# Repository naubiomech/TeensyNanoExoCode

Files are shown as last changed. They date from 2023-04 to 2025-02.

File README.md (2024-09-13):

# Teensy Nano Board

Diagram

This code uses two micronctrollers to control wearable robots. In order to
build the and flash the codebase check [here](Documentation/BUILD_AND_FLASH.md) and [here](https://github.com/naubiomech/TeensyNanoExoCode/blob/main/Documentation/README.md#how-to-deploy). If you would like to
contribute check [here](CONTRIBUTING.md) for more details. 
 
Check out the [Documentation Folder](/Documentation) for more details and C++ info.

Introductory videos on the system, its operation, and getting started can be found [here](https://drive.google.com/drive/folders/1eBydW7si7EmyGxdDkagQktmnZ7M4nHI4?usp=drive_link)

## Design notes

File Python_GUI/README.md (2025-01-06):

# OpenPythonAPI
## Overview

This program can run on any computer/terminal with python 3.12 installed. Libraries needed can be installed via pip (python's module manager)

Open source Application utilizing the OpenExo API to search, connect to, and controll NAU Biomecatronics Lab's OpenExo systems.

This project uses the MIT License.

The purpose of this project is to provide an open source solution for controlling the OpenExo system that is accessible to anyone and free to modify for their needs.

## Minimum System Requirements
**Operating System:**
* Windows 7 or newer
* macOS 10.9 or newer

**Python Version:**
* Python 3.2 or newer

**Hardware:**
* Processor: Dual-core (e.g., Intel Core i3 or AMD equivalent)
* Memory (RAM): 2 GB minimum (4 GB recommended)
* Storage: 100 MB free space (1 GB recommended for large datasets)
* Display: 768x1024 resolution minimum

## Intallation Guide
Video Guide: https://youtu.be/VnQeUM2K6Vg

BLE (Bluetooth Low Energy) is the heart of this project which provides a connection from this API to the exoskeletons. Bleak, a python library is used to handle all BLE operations. To find out more about Bleak click [here](https://bleak.readthedocs.io/en/latest/).

Other libraries that are required include:
 - `matplotlib`
 - `async_tkinter_loop`
 - `pygame`
 - `async_tkinter_loop`
 - `numpy`
 - `bleak`
 - `pandas`
 - `scikit-learn`
 - `micromlgen`
 - `matplotlib`
 - `pygame`
 - `pillow`

To install all of the libraries run the following command in your terminal from the project directory `python .\install_dependencies.py`

## Greneral WorkFlow
### Program control flow

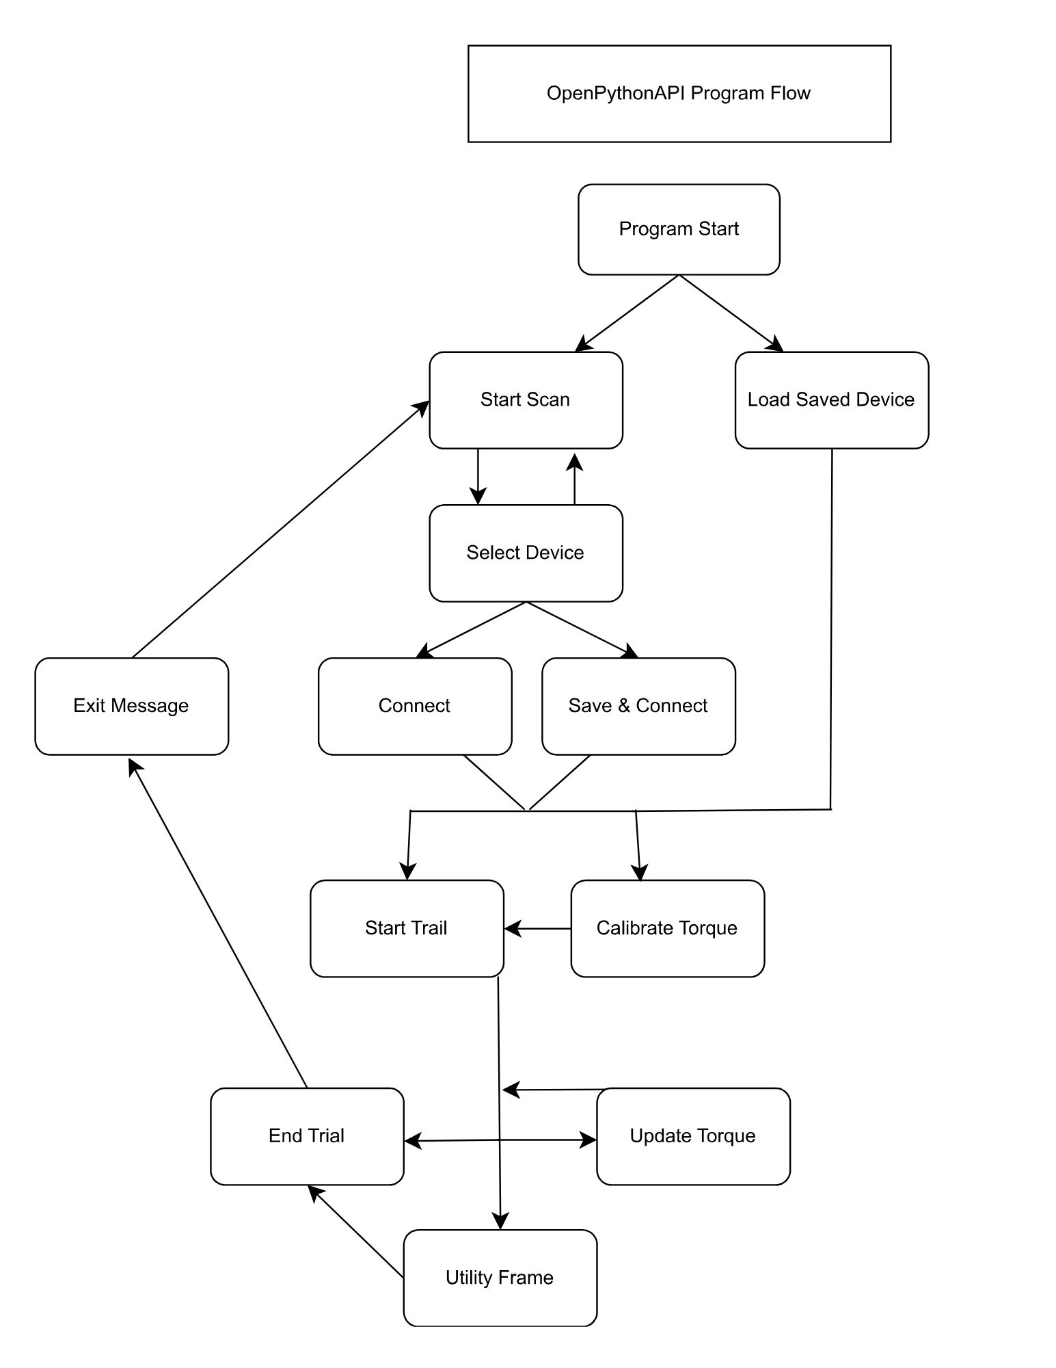
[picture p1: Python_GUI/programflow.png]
Program Control Flow


### Starting the Application
1. Ensure Bluetooth is enabled on your device.

2. Navigate to the project directory in your terminal.

3. Run the command:

`python3 GUI.py`

4. The GUI will launch, presenting various frames for interacting with the system

### Scanning for Devices

1. The application automatically scans for exoskeletons when the scan button is pressed.

2. If Bluetooth is disabled, an OS error will be displayed.

### Navigating the Interface

The GUI consists of several frames, each corresponding to specific functionalities:

* Scan Window: Initiate scanning and connect to devices.

* Active Trial: Monitor active trials and sessions.

* Biofeedback: Access real-time feedback tools.

* Machine Learning: Train and test models for personalized control.

* Update Torque: Change specific attributes of the exoskeleton

### Video Example

https://github.com/user-attachments/assets/6269629e-252b-4e77-b327-0914770ae9e3

## Adding a button

To add a button to the application, follow these steps:

1. Select a Frame: Choose a frame in the PythonApplication\views\ folder where you would like to add the button.

2. Integrate the Button: Here’s an example of how to add a button in a specific frame:

```python
class YourFrame(tk.Frame):
    def __init__(self, parent):
        super().__init__(parent)
        self.create_widgets()

    def create_widgets(self):
        my_button = tk.Button(
            self,
            text="My New Button",
            command=self.my_button_action
        )
        my_button.pack(pady=10)

    def my_button_action(self):
        print("My New Button was clicked!")
```
3. Functionality: Define what the button will do in the my_button_action method.

## Modifying the Graphing

To modify the graphing functionality, you can adjust the BasePlot class and its subclasses. Here's how to do it:

* Limit Points Displayed: In the `update_plot` method, modify the `max_points` variable to control how many points are displayed in the graph:

    ```python
    def update_plot(self, xValues, yValues, secondY, title):
        max_points = -20  # Change this value to display more or fewer points
        xValues = xValues[max_points:]
        yValues = yValues[max_points:]
        secondY = secondY[max_points:]
    ```
* Customize Axes and Titles: In the `update_plot` method, you can also adjust axis labels and titles:

    ```python
    self.ax.set_title(title)
    self.ax.set_xlabel("Time")
    self.ax.set_ylabel("Value")
    ```
* Implement Animation: Each plot subclass (e.g., `TopPlot`, `BottomPlot`) has an animate method that gathers data and updates the plot. Modify this method to change how data is sourced and displayed.

* For graph variable modification, refer to the Biofeedback graph description bellow.

## Adding a New Frame

To add a new frame to the application, follow these steps:

### Step 1: Create the New Frame Class

Create a new Python file in the views folder (e.g., newFeature.py).

Use the following template to define your new frame:

```python
    import tkinter as tk

        class NewFeature(tk.Frame):
        def __init__(self, parent, controller):
            super().__init__(parent)
            self.controller = controller

            label = tk.Label(self, text="New Feature Frame", font=("Arial", 24))
            label.pack(pady=20)

            button = tk.Button(self, text="Go to Scan Window",
                                command=lambda: controller.show_frame("ScanWindow"))
            button.pack(pady=10)
```
### Step 2: Update the ControllerApp Class

Open your main application file.

Import the new frame at the top:

`    from views.newFeature import NewFeature`

Add the new frame to the frames dictionary in the ControllerApp class:
```python
    for F in (ScanWindow, ActiveTrial, UpdateTorque, BioFeedback, MachineLearning, NewFeature):
```
### Step 3: Navigate to the New Frame

You can add a button in any existing frame to navigate to the new feature:
```python
    button = tk.Button(self, text="Go to New Feature",
                    command=lambda: controller.show_frame("NewFeature"))
    button.pack(pady=10)
```
## Biofeedback Frame
### Purpose

The Biofeedback frame provides visual and auditory feedback to users during training or analysis sessions. It aids participants in achieving specific performance goals by leveraging real-time sensor data.

### Signal Used in Biofeedback

1. Biofeedback currently utilizes force-sensitive resistors (FSRs) to monitor plantar pressure or estimated ankle power from exoskeleton sensors, but any sensor can be used.

2. The FSR data signal is accessed via the variable:

    `self.master.controller.deviceManager._realTimeProcessor._chart_data`

3. To switch between left and right leg signals, the variable updates dynamically based on the user’s selection 
    `._chart_data.leftFsr` or `._chart_data.rightFsr`

### Modifying the Signal

To modify the signal used in the biofeedback game:

1. Locate the FSRPlot class in the `chart.py` file.

2. Update the data source to the desired signal by modifying the variable:
    
    `self.master.controller.deviceManager._realTimeProcessor._chart_data` 

### Features and Buttons

#### Graphing

1. Graph Display: Visualizes pressure sensor data for real-time monitoring.

2. Target Lines: Displays a goal threshold on the graph when a target value is set.

#### Buttons

1. Back: Returns to the Active Trial frame.

2. Left/Right Leg Toggle: Switches the graph display between left and right leg FSR data.

3. Set Target Value: Opens a dialog box to input a target value for training.

    * Enables tracking progress toward specific performance goals.

4. Reset Target Value: Clears the target value and removes the goal line from the graph.

5. Mark Trial: Marks a specific event during data collection for later analysis.

6. Recalibrate FSRs: Initiates recalibration of the force-sensitive resistors to improve accuracy.

#### Notifications

1. Auditory Feedback: Plays a notification sound (e.g., `notification.wav`) when the user achieves a target.

2. Visual Feedback: The background temporarily changes color to indicate a successful target hit.

### Customization

To add or modify features in the Biofeedback frame, refer to the BioFeedback class in `biofeedback.py`.

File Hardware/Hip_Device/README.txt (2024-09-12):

Guiding Documentation to Assembling the device can be found at: https://drive.google.com/drive/folders/1gUSrXI882WxxylISEO5OPi-XwMUpgyXN?usp=drive_link

The Download for the CubeMars Motor Setup tool can be found in the same location.

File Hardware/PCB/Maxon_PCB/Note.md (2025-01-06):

More information on Maxon Motor Compatability (updated software, PCB, and hardware) coming soon!

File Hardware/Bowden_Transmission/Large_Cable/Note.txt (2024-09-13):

For the AK80 and Ak70 motors, if you are pursuing applications that require 
torque mangiutdes over 30 Nm, we recommend using a larger steel cable than the ones provided.

This necessitates a few modifications to the bill of materials and parts for the system, namely different:

Cable-Chain Interfaces
Bowden Tubes
Steel Cable
Crimps

We have included an updated BOM with this information to help you orient to that, the assembly process reamins the same

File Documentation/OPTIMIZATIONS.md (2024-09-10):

## Optimizations
- SPI direct memory access. Should change SPI time from 20 &mu;s per byte to the time to write the memory.
    - Teensy Datasheet 48.2.1 
        - Configure SPI
        - Teensy as controller and Nano as peripherial.
    - At top of loop teensy
        - Teensy flushes TX buffer and places fresh data data on TX Buffer.
        - Read if there are new messages from Nano and que completed messages.  Nano will read fresh data when this happens.
        - Teensy processes the que of new complete messages.  This should be a couple of messages and should be fine as the data sent will likely be smaller than data received.
        - Teensy runs the rest of the control loop.
    - Nano would place messages on tx buffer as bluetooth messages come in.
        - If the Nano is placing data when the Teensy reads the message will be sent over incomplete and will need to place the rest of the message afterwards which the Teensy will append when the next read happens.
        - Will need a message complete indicator at end of message.
        - Teensy que will also need a message complete flag to know if it needs to precess the message or if the message is incomplete start the next read by appending the rest of the message here. 

- BLEparser change from char representation to num bytes, expect 3 to 6x speed up.
    - This should be pretty straight forward as it can pretty much follow how messages are packed for the SPI.
    - I am not sure what issues will arise on the app side.
        - On the app you could just add a converter from num to char if you want to be lazy, but presumably you already have a char to num converter so I would recommend just cutting that out and fixing the stuff that breaks.
    
- CAN direct memory access, should cut about 250 &mu;s per motor.  Will still need a loop period of at least 250 &mu;s for the motors to return data.
    - https://www.pjrc.com/teensy/IMXRT1060RM_rev3.pdf 
        - CH 44
    - 6 mailboxes between TX and RX may have issues for a 4 motor setup without using a CAN bus per leg.  
        - All the complication with the limited mailboxes can be simplified by just using separate CAN buses for each leg, see other optimization below.  I have included how you could do it by switching mailboxes below, but don't do that if you don't have to.
            - Setup and Debug this with a bilateral uni-joint or unilateral multi-joint system so you can keep the motor count below 3 so you don't have to fiddle with all the mailbox shifting.  Then just setup the CAN2 below.
        - Can potentially use an ISR to mitigate this with a bit of loss in performance but will still be a big jump from where we are.
        - Can potentially switch mailbox type after emptied. Pair first TX (44.7.2) with first RX(44.7.4). When first TX is cleared becomes RX for next TX, or similar.  **DON'T WRITE A TX WITHOUT A CORESPONDING RX**.  You can write based on priority to help, highest priority first so you know it will return first.
            - This doesn't have to be first TX becomes second RX but you can play around to see what works.  Could have two TX RX pairs and two unpaired TX then the first two TX are emptied, change them to the RX for the unpaired TX and fill the second set of TX for writing.
        - 44.7.6 will also be useful.  In addition to the registers/memory map at the end.
    
- CAN bus per leg after DMA, roughly cut CAN time in half. Main control may be limiting time at this point at about 600&mu;s. Write at top, do controls, read at bottom.
    - Basically just follow above but with CAN2.  
    - Will need to update CAN code to make the CAN selectable 
    - Will need to attach a CAN object to the Leg instance rather than the Exo instance.

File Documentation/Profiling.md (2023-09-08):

Profiling is used to determine how long it takes for the computer to run your code. 
Typically more advanced software is used to automatically determine how long
each section of code takes to run, but Arduino does not provide any profiler software. 

To profile a section of code call micros() above the section of code and micros() below 
the section of code. Then Serial.print() the difference. ie:
        float start_time = micros();
        // The section of code
        float end_time = micros();
        Serial.print("Elapsed time in microseconds: ");
        Serail.println(end_time - start_time);

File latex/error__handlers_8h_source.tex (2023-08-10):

\doxysection{error\+\_\+handlers.\+h}
\hypertarget{error__handlers_8h_source}{}\label{error__handlers_8h_source}\index{ExoCode/src/error\_handlers.h@{ExoCode/src/error\_handlers.h}}
\mbox{\hyperlink{error__handlers_8h}{Go to the documentation of this file.}}
\begin{DoxyCode}{0}
\DoxyCodeLine{00001\ \textcolor{preprocessor}{\#ifndef\ ERROR\_HANDLERS\_H}}
\DoxyCodeLine{00002\ \textcolor{preprocessor}{\#define\ ERROR\_HANDLERS\_H}}
\DoxyCodeLine{00003\ }
\DoxyCodeLine{00004\ \textcolor{preprocessor}{\#if\ defined(ARDUINO\_TEENSY36)\ \ ||\ defined(ARDUINO\_TEENSY41)}}
\DoxyCodeLine{00005\ }
\DoxyCodeLine{00006\ \textcolor{preprocessor}{\#include\ "{}\mbox{\hyperlink{_exo_data_8h}{ExoData.h}}"{}}}
\DoxyCodeLine{00007\ \textcolor{preprocessor}{\#include\ "{}\mbox{\hyperlink{_exo_8h}{Exo.h}}"{}}}
\DoxyCodeLine{00008\ \textcolor{preprocessor}{\#include\ "{}\mbox{\hyperlink{error__types_8h}{error\_types.h}}"{}}}
\DoxyCodeLine{00009\ \textcolor{preprocessor}{\#include\ "{}\mbox{\hyperlink{uart__commands_8h}{uart\_commands.h}}"{}}}
\DoxyCodeLine{00010\ }
\DoxyCodeLine{00011\ \textcolor{comment}{//\ Handles\ errors}}
\DoxyCodeLine{00012\ \textcolor{keyword}{namespace\ }error\_handlers}
\DoxyCodeLine{00013\ \{}
\DoxyCodeLine{00014\ }
\DoxyCodeLine{00015\ \ \ \ \ \textcolor{keywordtype}{void}\ soft(Exo*\ exo,\ \mbox{\hyperlink{class_exo_data}{ExoData}}*\ exo\_data,\ \textcolor{keywordtype}{int}\ error\_code)}
\DoxyCodeLine{00016\ \ \ \ \ \{}
\DoxyCodeLine{00017\ \ \ \ \ \ \ \ \ \textcolor{comment}{//\ TODO:\ Recalibrate/Warn\ user}}
\DoxyCodeLine{00018\ }
\DoxyCodeLine{00019\ \ \ \ \ \ \ \ \ \textcolor{keywordflow}{return};}
\DoxyCodeLine{00020\ \ \ \ \ \}}
\DoxyCodeLine{00021\ \ \ \ \ \textcolor{keywordtype}{void}\ hard(Exo*\ exo,\ \mbox{\hyperlink{class_exo_data}{ExoData}}*\ exo\_data,\ \textcolor{keywordtype}{int}\ error\_code)}
\DoxyCodeLine{00022\ \ \ \ \ \{}
\DoxyCodeLine{00023\ \ \ \ \ \ \ \ \ exo\_data-\/>\mbox{\hyperlink{class_exo_data_a2aa97c53cd67d549d14b349cf1b46f0e}{for\_each\_joint}}([](\mbox{\hyperlink{class_joint_data}{JointData}}*\ joint\_data,\ \textcolor{keywordtype}{float}*\ args)\ \{\textcolor{keywordflow}{if}\ (joint\_data-\/>\mbox{\hyperlink{class_joint_data_ac92eaeab50564303d8c8ca0febd44c12}{is\_used}})\ joint\_data-\/>\mbox{\hyperlink{class_joint_data_afaead532774a6d60394f3667838d61d1}{motor}}.\mbox{\hyperlink{class_motor_data_a4b909a13e4ac0eb7c3f05a1de2b0dc60}{enabled}}\ =\ 0;\});}
\DoxyCodeLine{00024\ \ \ \ \ \ \ \ \ \textcolor{keywordflow}{return};}
\DoxyCodeLine{00025\ \ \ \ \ \}}
\DoxyCodeLine{00026\ \ \ \ \ \textcolor{keywordtype}{void}\ fatal(Exo*\ exo,\ \mbox{\hyperlink{class_exo_data}{ExoData}}*\ exo\_data,\ \textcolor{keywordtype}{int}\ error\_code)}
\DoxyCodeLine{00027\ \ \ \ \ \{}
\DoxyCodeLine{00028\ \ \ \ \ \ \ \ \ exo\_data-\/>\mbox{\hyperlink{class_exo_data_a2aa97c53cd67d549d14b349cf1b46f0e}{for\_each\_joint}}([](\mbox{\hyperlink{class_joint_data}{JointData}}*\ joint\_data,\ \textcolor{keywordtype}{float}*\ args)\ \{\textcolor{keywordflow}{if}\ (joint\_data-\/>\mbox{\hyperlink{class_joint_data_ac92eaeab50564303d8c8ca0febd44c12}{is\_used}})\ joint\_data-\/>\mbox{\hyperlink{class_joint_data_afaead532774a6d60394f3667838d61d1}{motor}}.\mbox{\hyperlink{class_motor_data_a4b909a13e4ac0eb7c3f05a1de2b0dc60}{enabled}}\ =\ 0;\});}
\DoxyCodeLine{00029\ \ \ \ \ \ \ \ \ \textcolor{keywordflow}{return};}
\DoxyCodeLine{00030\ \ \ \ \ \}}
\DoxyCodeLine{00031\ \}}
\DoxyCodeLine{00032\ }
\DoxyCodeLine{00033\ \textcolor{preprocessor}{\#endif}}
\DoxyCodeLine{00034\ }
\DoxyCodeLine{00035\ \textcolor{preprocessor}{\#endif\ }\textcolor{comment}{//\ defined(ARDUINO\_TEENSY36)\ \ ||\ defined(ARDUINO\_TEENSY41)}}

\end{DoxyCode}

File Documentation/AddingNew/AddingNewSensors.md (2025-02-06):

# Adding New Sensors

## Overview
In our codebase, sensor integration varies depending on the sensor. Below, we list some of the sensors we've tested or integrated that are compatible with our codebase:
- **Analog input**
    - Force sensitive resistor
    - Torque sensor (strain gauge)
    - Angle sensor (AS5600; hall effect)
- **Bus protocol**
    - I2C (Teensy-Nano communication)
    - UART (Teensy-Nano communication)
    - CAN (Teensy-Motor communication)
    - SPI (Teensy-SD Card interface)

Here, we'll demonstrate how the Teensy communicates with sensors using an example of an analog input sensor and another example with the I2C protocol.

---

## Analog input
For an analog sensor, such as the torque sensor we used for exoskeleton torque feedback control, the fundamental operation involves using `analogRead()` on the signal pin to get the sensor reading (or its amplified value):

```
float current_reading =  analogRead(_pin)*torque_calibration::AI_CNT_TO_V;
```

### Notes from PJRC:
- None of the pins on the Teensy are 5-volt tolerate, and the input voltage range is fixed at 0 to 3.3 volts.
- `analogReference()` has no effect on Teensy 4.1

*Sidenote*: If you need to use `digitalRead()`, make sure to set the appropriate pin mode using `pinMode()` with values such as `INPUT` or `INPUT_PULLUP`. Refer to the user manual of the sensor or peripheral in use.

### More examples on `analogRead()`
The following `.cpp` files utilize `analogRead()`:
- `AnkleAngles.cpp`
- `FSR.cpp`
- `TorqueSensor.cpp`

### Available analog pins
If you're using our reference printed circuit boards (PCB), check the PCB design documentation for the list of available analog pins. You can always use stacking headers for Teensy 4.1 to make certain pins easier to access.

---

## Bus protocols
Unlike data links that use analog signals, a bus acts as a highway for digital signals carrying encoded messages, enabling much faster data transmissions at higher frequencies. You can find a comparison of some of the bus protocols used in our codebase [here](https://www.totalphase.com/blog/2021/12/i2c-vs-spi-vs-uart-introduction-and-comparison-similarities-differences/ "I2C vs SPI vs UART").

### I2C in our codebase—A detailed example
Noah Enlow put together some great documentation detailing how I2C works in our codebase, and we're excited to share it here.

<details open>

  <summary><strong>Click to fold</strong></summary>

- I2C works by sending a series of bytes that represent the information you're wanting to send. The Wire library in arduino does not automatically interpret the bytes being sent/recieved into the intended data type (e.g. float or int). Therefore, in order to send data over I2C with the wire library, the data must be converted into its respective representation in bytes. The simplest and most efficient way to do this is to use a union. 

- Unions in arduino (and C++) function similar to structs. However, with unions, the data stored within is stored in a single location in memory and can be accessed as any data type desired (such as float or int). Thus, a union allows you to access the same raw data in multiple ways. 

- This is useful for sending data over I2C because now we can collect our data from a sensor (say float data from an accelerometer), store it in a union, and then access that same data as bytes when we're ready to send it via I2C. On the receiving device, we essentially do the opposite. We receive the incoming bytes into a union, and then access the data as floats again.
The scheme is:
```
    float -> convert to bytes -> send over I2C -> receive as bytes -> convert back to float
```
- Below is a demonstration of how to send float data over I2C using a union (the process is identical for other data types such as ints or doubles):

    1. First define the union: 
    ```
        union Data                      # Data is the name of the union
        {
            float data_as_float;        # Representation of the data as a float
            byte data_as_bytes[4];      # Represntation of the data as a vector of bytes (must specify the size, floats are 4 bytes)
        };
    ```

    2. Now store the data you'll be sending:
    ```
        Data.data_as_float = data_to_be_sent;	# data_to_be_sent is a dummy variable representing the data you want to send
    ```

    3. Send via I2C using the Arduino Wire library:
    ```
        void sendEvent()                         # sendEvent() is called in your main loop whenever you are ready to send the data
        {													
            Wire.write(Data.data_as_bytes, sizeof(Data.data_as_bytes));
        }
    ```

- Now to recieve the data that has been sent. We'll create an identical union on the device requesting the data (primary) to make it more intelligible, however the union need not be identical.
    1. Define a union on the device receiving the data:
    ```
        union Data                      # Data is the name of the union
        {                	
            float data_as_float;        # Representation of the data as a float
            byte data_as_bytes[4];      # Representation of the data as a vector of bytes (must specify the size, floats are 4 bytes)
        };
    ```

    2. Now request the data from the peripheral (secondary) device, which in this case is the one doing the sending. Because the data is coming in as individual bytes, we'll need a for loop to iterate through those bytes and append them to the vector of bytes contained in the union we just defined.
    ```
        Wire.requestFrom(PERIPHERAL_ADDRESS, 4);
        for(int i=0; i<4; i++)
        {
            Data.data_as_bytes[i] = Wire.read();
        }
    ```
    3. Now to access that data as a float again:
    ```
        float data_recieved = Data.data_as_float;
    ```

- In summary, a union was created on our peripheral device (the device sending) to store the float data and send it as bytes over I2C. Another identical union was created on our primary device, which in this case is the one we want to recieve the data. A for loop is used on the primary to iteratively append the bytes being recieved to the byte-type variable in the union. Once this is done, the data recieved can then be accesed as a float again through the union.

</details>

---

### More examples on bus protocols
The following `.cpp` or `.h` files utilize I2C:
- `Battery.cpp`
- `I2CHandler.h`
- `RealTimeI2C.cpp`
- `ThIMU.h`

The following `.cpp` file utilize SPI:
- `ParamsFromSD.cpp`

The following `.cpp` or `.h` files utilize UART:
- `ble_commands.h`
- `ComsMCU.cpp` and `ComsMCU.h`
- `ErrorReporter.h`
- `Exo.cpp`
- `uart_commands.h`
- `UARTHandler.cpp`

The following `.cpp` or `.h` files utilize CAN:
- `CAN.h`
- `Motor.cpp`

### Available pins for bus protocols
If you're using our reference printed circuit boards (PCB), check the PCB design documentation for the list of available pins for bus protocols. You can always use stacking headers with Teensy 4.1 to make certain pins easier to access.

---
To ensure a sensor readings are accessible from various locations, we've created the following procedures to help you embed your new sensor into the codebase.
## Location—Where should I write the sensor code?
Because the sensors don't have a common interface it is a bit more straight forward to add new ones.
The main things you will need to decide is what part of the system makes the most sense for the part to live, e.g. exo, side, joint.

## Create the Sensor
The sensor should be its own class.
You will need to create a .h and .cpp file in the src folder.
The sensor class will have all the functions that you need to use the class, below you can find an example to build from.
This example is an outline of what would be in the header(.h) file.

```
class CLASS_NAME
{
    /*
     * public functions are ones that can be called from outside the class.
     */
    public: 
        /*
         * Constuctor for the class
         */
        CLASS_NAME(int pin);// you may not need the pin if it doesn't use an analog input.
        
        /*
         * Checks if the sensor needs to be calibrated and returns if the calibration is done.
         * This should be called every time the containing system is run.
         * Depending on your system you may not need to calibrate.
         */
        bool calibrate(bool do_calibrate);
        
        /*
         * Used to read the sensor and returns the value.
         * If you need multiple returns you will need to pass the place the date will go by pointer: 
         * void read(float* val0, float* val1);
         * Where it will be called using:
         * read(&place_to_store_val0, &place_to_store_val1);
         */
         float read();
    /*
     * Private functions and variables can only be called from within the class.
     */
    private:
        
        /* 
         * Sample private function this will be very dependent on what the system needs.
         */
        void _sample_function();
        
        // The pin the sensor is connected to.
        int _pin;
        
        // sample private variable for the sensor.
        float _sample_var;
};
```

## Migrating to the Main Code.

### Board.h
For each board that will use the sensor add the pin that each sensor will use.
If there are four sensors you will need to define 4 pins.
This assumes it is an analog sensor, if you are using a different type of sensor you can define the things that sensor needs here.
Make sure that that pin is free, this should be easier if you design the PCB first.

### System Containing Sensor Data .h
Create a variable to store the the data from the sensor.
If the sensor will be at the side level this will be in the SideData class, if it is the joint the JointData class, etc.
Additionally if the sensor will need to be calibrated make a variable to store that state;
```
float sensor_reading;
bool sensor_calibrate;
```

### System Containing Sensor Data .cpp
In the constructor related the the .h file you just modified, initialize the value to to what you want it to start at, this will often be 0.

```
sensor_reading = 0;
sensor_calibrate = false;
```

### System Containing Sensor.h
This will be Side.h if the sensor is at the side level or Joint.h if it is at the joint level, etc.
Add the include for the sensor, ```#include Sensor.h```, that you created.
Within the class; Side, Joint, etc.; declare an instance of the class ```SensorClass new_instance_of_sensor;```
Create as many instances as you need.

### System Containing Sensor.cpp
1. Within the .cpp file related to the .h file you just changed you need to call the constructor for the instances of the class you just declared.
This will be done in the initializer list.
For example for a joint level sensor:
```
Joint::Joint(config_defs::joint_id id, uint8_t* config_to_send)
: motor(id, config_to_send)
, controller(id, config_to_send)
, new_instance_of_sensor(pin_to_use)
{
```

2. Add a call to the sensor.read() in the containing classes read referencing the sensor data we already made.
For a joint level sensor:
``` 
_joint_data->sensor_reading = new_instance_of_sensor.read();
```

3. Add a call to the sensor.calibrate(do_calibrate) in the containing classes read referencing the sensor data we already made.
For a joint level sensor:
``` 
_joint_data->sensor_calibrate = new_instance_of_sensor.calibrate(_joint_data->sensor_calibrate);
```

This will get called every time the joint is run and if the calibrate variable is set to true will calibrate the sensor.

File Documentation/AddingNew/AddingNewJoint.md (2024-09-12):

# Adding a new joint

## Exocode.ini
1. Line 118: Add joint to the debug statement determining if it is used.
2. Line 148: Add joint to if statements relating to whether or not the joint is used
	- Copy the if statements for the left and right side for one joint (e.g., hip) and paste below last joint
	- Modify the joint to be named after the new joint you are adding. 
3. Line 398: Add in calibrate torque sensor and enable motors for the joint while in headless mode
	- Copy the formatting from another joint, make sure to do both left and right side.
4. Line 540: This section sets the controller for each joint (while in headless mode), copy the formatting for one joint and rename it to your new joint
	- Need to pull in the default controller information from the config
	- Then set the controller based on this configuration information

## ParseIni.h
1. Update exo_name in the config_defs namespace, make sure to encompass any configuration you would want with that joint (e.g., bilateral, unilateral, multi-joint)
2. Update JointType in the config_defs namespace
3. Update joint_id to utilize the proper byte for the new joint (see comment in code)
	- make sure to update the left and right joint information following the format as well. 
4. Add a new enum class for the joint's controllers following the other joints' formatting
	- Add in any controllers associated with the joint if there are any ready, you can always come back to this following "AddNewController"
5. Update the static const int variables at the end of the config_defs namespace to account for the new joint.
6. In config_map namespace, update the IniKeyCode exo_name to account for all the configurations made in the exo_name enum class in config_defs
7. In config_map namespace, add in a new IniKeyCode for the joint's controllers (following the format for the other joints)
	- Make sure to update the terminology of the entire section (i.e., the section after config_defs:: in the main text of it
8. Update the ConfigData struct at the end to match 
 
## ParseIni.cpp
1. Line 174 -> Onward: Copy template in each section to add in new joint so that it is formatted same as other joints.

## ExoData.h
1. In the functions "for_each_joint", add in the new joint following the format of the previous joints
    
## ExoData.cpp
1. In the function "get_used_joints" (36), add in the new joint following the format of the other joints already there, make sure to do both the left and right sides
2. In the function "get_joint_with" (59), add in the new joint following the format of the other joints already there, make sure to do both the left and right sides
3. Similarly, in the function "print" add in the prints of the new joint for each side (left and right) following the establish formatting.

## UART_commands.h
1. Update the function "get_config" (Line 196) with the config_defs you added in ParseIni.h, refer to that file and look at the added "static const int" at the end of the config_defs namespace
2. Similarly, update the function "update_config" (Line 227) with the config_defs you added in ParseIni.h, refer to that file and look at the added "static const int" at the end of the config_defs namespace
3. In "get_real_time_data" (Line 306), add in a new case in the switch statement corresponding to the bilateral configuration of the joint and for any multi-joint instances. You can send up to 10 data points at a time using the established formmating.

## Side.h
1. Create Joint object specific to the joint that you are adding (Line 158, is where the other joint objects are specificed, follow their formmating)

## Side.cpp
1. Add in the new joint object you just created in the .h file into the constructer of the side following the format of the other joints in the constructer 
2. In the "disable_motors" function (Line 58), add in the new joint following the formatting of the other joints.
3. In the "read_data" function (Line 98), add in an if statment at the end (Line 142) that reads the data specific to the joint object (see other joints for formatting)
4. In the "check_calibration" function (Line 161), add in a if statment at the end of the end of the function (Line 189) that checks the calibration specific to the new joint object (see other joints for formatting)
5. In the "update_motor_cmds" function (Line 534), add in a new if statement at the end that runs the new joint functions (see other joints for formatting)

## SideData.h
1. Line 42: Create a new instance of jointdata and create an object for it for your new joint (see other joints for formatting)

## SideData.cpp
1. Add in the new joint object you just created in the .h file into the constructer of the sidedata following the format of the other joints in the constructer 
2. On the last line add in a new statement reconfiguring the joint you just added (see other joints for formatting). 

## Joint.h
1. Create a class specific to the joint, make sure it inherits the public _joint class
	- Make sure to include a joint specific constructor and destructor and the two essential functions "run_joint" and "set_controller" in the public section.
	- In the private section call instances of the controller class for those specific to the joint and create new objects for those classes
	- Aka copy what the other joints did and change the names and controllers

## Joint.cpp
1.	Add the new joint to the Joint Debug statement (Line 40) in the _Joint constructor at the begining
2. 	In the function "get_torque_sensor_pin" add a new case to the switch statment specific to your added joint following the format of the other joints
3.	Similarly, in the function "get_motor_enable_pin", add a new case to the switch statement specific to your added joint.
4. 	Add in the new joint class following the format of the other joints
	- Make sure to include all the controller instances in the initializer list in addition to the _Joint instance 
	- Update the debug statements to refelct the newly added joint
	- Update the Switch Case that creates an object for the specific motor type 
	- Update the call of the "set_controller" function at the end of the constructor
	- Update the "run_joint" function 
		- update the debug statements, the rest is non-joint specific 
	-Update the "set_controller" function 
		- Update debug statement
		- Update switch case for controller ID

## JointData.cpp
1. Update the switch statement in the JointData initializer to include the new joint (Line 31) 
	- Include the portion that sets the value for "is_used" and the if statment to flip the direction 
	- Follow the format of the other joints in this section 
2. Repeat this process for the "reconfigure" function 

## Motor.cpp
1. Update the switch statment in the motor initializer (Line 39) to include the new joint

## MotorData.cpp
1.	Update the switch statement in the initalizer (Line 16) to include the new joint
	- Include both the gearing and the flip direction portions
2. 	Repeat this process for the "reconfigure" function 

## ControllerData.cpp
1.	Update the switch statement in the constructor (Line 16) to include the new joint
2. 	Repeat process for the "reconfigure" function (Line 56)

## Controller.cpp
1.	Update the switch statement in the constructor of _Controller to incorporate the new joint (Line 35)

## ble_commands.h
1. In the function "new_trq" update the joint_id mapping to encompass the new joint (make sure to do both left and right side)
	- Make sure you update the joint id number in these statments to follow a logical order (e.g., left_hip = 1, left knee = 2, left ankle = 3, left elbow = 4, ....)
2. Update the if statement associating controller data with the joint ID

## ParamsfromSD.h
1.	In the controller_parameter_filenames namespace, add in a ParamFilenameKey for the new joint and associate the appropriate controllers

## ParamsfromSD.cpp
1.	In the "print_param_error_message" function, update the switch statment to include the new joint
	- Make sure to update the actual switch statment itself during this process (Line 10) in addition to adding the new case 
2. In the "set_controller_params" function 
	- Copy a case of the switch statement from another joint below the last added joint, update any reference to the specific joint (e.g., elbow, ankle,...) to your new joint
	- There is a lot going on here so make sure you did not miss any reference to the specific joint in this section. 
## RealTimeI2C.h
1.	In the rt_data namespace update the static int RT_LEN to include the configurations you added to "get_real_time_data" in uart_commands.h

## StatusDefs.h
1. In the messages namespace, update the error messages with the joint you are adding
	- Torque Sensor, Motor, Controller portions for both side (left, right)
	- Make sure to go back and update the numbering 
2. Update the nomenclature of the remaining "error_to_be_used" if there are any 

## StatusDefs.cpp
1.	Update the switch statment in "print_status_message" to include the new joint
	- Torque Sensor, Motor, Controller for both sides (left, right)

## StatusLED.h
1.	Update IdxRemap status_led_idx in the status_led_defs namespace with the new joint, follow the other joints for formatting
2. 	Remove the no longer valid "error_to_be_used_#" sections 

## Config.ini
1.	Copy the information for one joint setting (e.g., bilateralHipAnkle) and add paste it later on 
2. 	Rename the newly added formatting for your newly added joint
3. 	Update the contained information appropriatly

## SD Card
1. Make a jointControllers folder with the .csv for the controllers specific to the joint

## Python GUI - ActiveTrialSettings.py
1. Find the section titled "jointMap"
	- Add in the new joint name and incrament the int value in the section following the format of the other joints.
2. In the UpdateTorque Class, update the string list in "values" under the section labeled "Joint Select" with the joint name (e.g., Left elbow, right elbow)

## Python GUI - exoDeviceManager.py
1. Find "jointDictionary" under the ExoDeviceManager Class
	- Update the directory with the joint numbers you added in "ActiveTrialSettings" and associate with the Motor ID number you set the motor to via the RLink and in the software
	- Follow the format of the other joints (e.g., 1: 33. 0 = "Left Hip with an ID of 33")

## Done
It should now be good to go.

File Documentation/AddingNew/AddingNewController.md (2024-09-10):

# Adding a new controller

## parseIni.h
1. Go to the config_defs namespace and the joint(s) you are creating a controller for and add it to the enum class so we can reference it.
2. Go to the config_map namespace and add for the joint(s) you are creating a controller for and add the name that will be used in the config.ini file.

## ControllerData.h
1. Go to the controller_defs namespace and add a namespace for your controller following the template from the other controllers
    - Create idx values that will be used to access the different parameters (remember this is 0 indexed)
    - Add a num_parameter value that stores the number of parameters the controller needs.
    - if this number is larger than the max_parameters in controller_defs, change max_parameters to your value. 

## Controller.h
1. Under Controller.h create a new controller that inherits the _Controller class.
    - this must have:
        - A constructor that takes in the joint id and exo_data pointer.
        - A destructor
        - And a calc_motor_cmd() function that returns the torque command in mNm.
    - Additional private functions or variables can be added as needed but the only calls to a controller will be to the three required functions.

## ControllerData.h
1. This section is optional, at the bottom of ControllerData.h you can add any variables for your controller that you would like to be able to plot, these would be in place of the variables defined in Controller.h. 
	- To assign value to these parameters in Controller.cpp, you need to use the following formatting:
		- controller_data->NAMEOFVARIABLE = VALUE;
		
## Controller.cpp
1. Define all the functions for the controller.  
    - An initializer list for _Controller will be needed when calling the constructor.  
    
## Joint.h
1. Under the joint(s) (hip, knee, ankle) the controller is valid for, add an object to the new controller.

## Joint.cpp
1. For the joint(s) the controller is valid for:
    1. Add the constructor for the object you just added to the initializer list.
    2. In set_controller(), add the controller to the switch case, referencing the joint controller namespace in the config_defs namespace.  
        - Use the existing controllers for the template
        - This changes which controller object the _controller pointer is using.
        - Don't forget to add the 'break;' at the end of the switch case!
	- Note: The switch case references the config_defs name and the value passed to _controller references the object created in Joint.h

## Create parameter file
1. In the SDCard folder go to the joint your controller is for.
2. Create a new parameter csv file, I would recommend just copying one of the existing ones
3. The first cell in the first line is the number of lines in the header.  Parameters will start being read after this number of lines.
4. The first cell in the second line is the number of parameters to read, this should match what you put in ControllerData.h.  This was easier than trying to get the reading a full line of floats to be robust.
5. After the header, put the parameter sets you would like to use, one set per line.  The parameters should be listed in the index order from ControllerData.h.  The first set will be default.
6. If the controller is multi joint copy to the other joint folders.

## ParamsFromSD.h
1. In the controller_parameter_filenames namespace go to the appropriate joint
2. Link the controller id from config_defs and the path on the SD card for the parameter file you just created.

## uart_commands.h
1. This section is optional, if you want to plot or save one on of the variables you created in ControllerData.h:
	- In get_real_time_data()
		- Find the case for the joint you are using the controller for (e.g., bilateral_hip)
		- Assign the variable to one of the data spots in the rx.msg (e.g., rx_msg.data[0])
			- If the variable is specific to the controller, use the following formatting:
				- rx_msg.data[#] = exo_data->NAME_side.JOINT.controller.VARIABLENAME;
					- Here: NAME_side should either be left_side or right_side, JOINT should be the joint you are working with, and VARIABLENAME is the name of the variable you want to plot.
			- You can also plot variables specific to a side (defined in SideData.h) using the following formatting:
				- rx_msg.data[#] = exo_data->NAME_side.VARIABLENAME;

## Done
It should now be good to go.  You will need to change the controller and update the parameters.

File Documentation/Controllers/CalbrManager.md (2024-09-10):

# Calibration Manager Controller

## Description
This controller applies a small, constant torque while printing statements of relevance (command value/sign, torque sensor value/sign, angle sensor value/sign) to the Arduino Serial Monitor. 

## Parameters
There are no user defined parameters associated with this controller. 

## Purposes
After you have built an exo, one of the first things to check is the motor directions and the signs (positive/negative) of any of your external sensors (torque, angle, etc.). 
Having correct motor directions is important as it allows the exo controller designers to focus on the control itself, knowing that, if calibrated properly before use, the exo assistance will always be in the designed directions. 
The same principle applies for the sensors involved with control. Since PID control is implemented in many of our exo controllers, it is crucial to make sure that the directions match. 
This article will elaborate how to conduct the direction calibration using the CalibrManager controller. 
On each exo, this calibration process only needs to be done **once**, its results will need to be **manually** saved on the SD card and will be loaded **automatically** every time the exo starts up.

## Motor directions
When designing a controller, the values returned from the "calc_motor_cmd()" function determines the motor torque command (feedforward). To ease the controller design process, we propose that controller designers follow the following direction definitions for torque commands:
- At both ankle joints: Positive for Dorsiflexion, and negative for Plantarflexion
- At both knee joints: Positive for Extension, and negative for Flexion
- At both hip joints: Positve for Flexion, and negative for Extension
- At both shoulder joints: Positive for Flexion, and negative for Extension
- At both elbow joints: Positive for Flexion, and negative for Extension

In summary, this follows the Right-hand rule.

## Torque sensor signs (positive/negative)
Following the motor direction definitions, we need to verify that, when the motor supplies a positive torque command, the torque sensors, when zeroed properly, also returns a positive reading when the motor shaft is not spinning.

# How to calibrate
1. To calibrate, set Direction Calibration Manager as the default controller for the current exo. Connect the Teensy to a computer through USB, open up the Arduino Serial monitor. Connect the exo (Arduino Nano) with the python app, power on the exo and start a new session. The Direction Calibration Manager will send a positive torque command (3.5 Nm by default) to each motor.
2. Feel each torque through, for example, the foot plates on an ankle exo. If the torque applied on, for example, the left foot plate, is not causing it to rotate in the positive direction (see above for the specific directions), flip the motor direction for the left side. Flipping the motor direction is done by modifying the "config.ini" on the SD card.
3. After modifying all motor directions (if needed), start over again, and this time focus on the sensor readings (e.g., torque, angle) shown on the Arduino Serial Monitor. Feel the motor torque through, for example, a foot plate on an ankle exo, manually move the foot plate back to its neutral position, 0 degree for example. If the corresponding sensor does not return a postive value, flip the sensor direction by modifying the "config.ini" on the microSD card. Go through all torque sensors (if needed).

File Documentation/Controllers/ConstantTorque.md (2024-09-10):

# Constant Torque Controller

## Description
This controller attempts to apply a constant torque to the joint.  
This can be done with or without closed loop control.

## Parameters
Parameter index order can be found in [ControllerData.h](/ExoCode/src/ControllerData.h).
- amplitude - Magnitude of the applied torque, in Nm
- direction - Flag to flip the direction of the applied torque
- alpha - Filtering term for exponentially wieghted moving average (EWMA) filter, used on torque sensor to cut down on noise. The lower this value the higher the delay caused by the filtering. 
- use_pid - This flag turns PID on(1) or off(0)
- p_gain - Proportional gain for closed loop controls
- i_gain - Integral gain for closed loop controls
- d_gain - Derivative gain for closed loop controls

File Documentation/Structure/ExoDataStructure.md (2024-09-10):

```
ExoData
{
    reconfigure(uint8_t* config_to_send)
    for_each_joint(for_each_joint_function_t function)
    
    status
    sync_led_state
    estop  
    
    SideData : left_side, right_side
    {
        reconfigure(uint8_t* config_to_send)
        
        percent_gait
        expected_step_duration
        heel_fsr
        toe_fsr 
        ground_strike 
        expected_duration_window_upper_coeff
        expected_duration_window_lower_coeff
        is_left
        is_used
        do_calibration_toe_fsr
        do_calibration_refinement_toe_fsr
        do_calibration_heel_fsr
        do_calibration_refinement_heel_fsr
        
        JointData : hip, knee, ankle
        {
            reconfigure(uint8_t* config_to_send) 
            
            id
            torque_reading
            is_left
            is_used 
            flip_direction
            calibrate_torque_sensor 
            position
            velocity
            
            motor
            {
                id
                motor_type
                is_left
                is_on
                enabled
                do_zero
                flip_direction
                gearing
                p 
                p_des
                v
                v_des
                i
                t_ff
                kp
                kd
            } 
            
            controller
            {
                reconfigure(uint8_t* config_to_send) 
                
                controller
                joint
                setpoint
                parameters[controller_defs::max_parameters]
            }
        }  
    }
}
```

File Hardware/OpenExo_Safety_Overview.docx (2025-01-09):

# Open Exo Safety Document

Purpose 2

General Safety Recommendations 2

Electrical Hazards 2

Electrical Shock 2

Fire 2

Temperature Hazards 3

Heat 3

Physical Hazards 3

Tripping and Falling 3

Cuts/Scrapes/Splinters 3

Pinch 4

Blunt Force 4

# Purpose

The purpose of this document is to outline safety recommendations and hazard mitigation strategies for the operation and maintenance of OpenExo and its configurations to ensure the safety of users and bystanders.

# General Safety Recommendations

- Never operate or work on an OpenExo device without someone else present.
- Wear eye protection when working on or inspecting the device closely while it is powered on.
- Never touch a printed circuit board while a battery is plugged in.
- Never leave a battery plugged in when not in use.
- Assume the device’s motors will activate when powered on and take necessary precautions.
- Always inspect the device for loose connections, worn parts, and other signs of damage before use.
- Train all operators in the safe use of the device.

# Electrical Hazards

## Electrical Shock

Serious electrical shock is a hazard for any battery used to power OpenExo (e.g., 6S LiPo). These batteries can also cause burns to the skin or even death if mishandled. Ensure that no bare wires are exposed and that the PCB is enclosed to prevent electrical shock. Never touch two ends of a battery terminal, lead, or PCB with two hands, which could result in current passing through and stopping your heart.

Always handle batteries and electrical components with dry hands.

Ensure the battery or any other source of electrical power is not connected to the device when servicing.

## Fire

Improper care for the battery can lead to a fire. If the battery shows any of the following signs, dispose of it in a safe manner and do not use it any further:

- Swelling or bulging
- Leaking
- Cracks, dents, or punctures
- Overheating

Furthermore, shorting the terminals of the battery can cause the battery to heat rapidly, leading to thermal runaway and a fire. Ensure that wires directly connected to the battery are properly insulated and there is no possibility of a short circuit. Always charge batteries in a fireproof container using an appropriate charger and never leave batteries unattended during charging.

# Temperature Hazards

## Heat

The motors used on the exoskeleton have a rated operating temperature of up to 100 °C. These temperatures well exceed the recommendations of the American Society for Testing and Materials’ temperature safety recommendations (C 1055-99), which states that five seconds of contact with temperatures over 60 °C may lead to epidermal injury. We advise avoiding prolonged contact with the exposed surface of the motors and suggest utilizing designed heat shieldings for all OpenExo configurations to reduce the chance of injury in instances of accidental prolonged contact.

# Physical Hazards

## Tripping and Falling

As with any experimental device, there are potential risks related to device modification (e.g., alteration to hardware components such as sensors, alterations to software such as controllers). Following alteration or prolonged usage (where sensor wear and failure may be more common), we recommend operating the device with caution upon startup as it may behave in unexpected manners that could lead to adverse events such as trips or falls.

It is highly recommended that safety harnesses are worn during operation when possible, particularly when in use on equipment like treadmills or stair steppers.

## Cuts/Scrapes/Splinters

There are a few possible sources of cuts, scrapes, and splinters on the exoskeleton.

- The screws facing outward on the thermoformed motor mounts should be fitted with the rubber caps indicated in the assembly guide to avoid scratches.
- If zip ties are used to fasten wires in place, the burs leftover should be trimmed and filed down to avoid cuts and scrapes.
- Any sharp points or corners left over from the fabrication process should be ground down to again avoid cuts and scrapes.
- The carbon fiber uprights used to deliver the torque from the motors to the users legs should be kept in good condition and checked for any burrs, cracks, or splinters to avoid injury to the user.
- When utilizing the bodwen-transmission system there is a risk that the steel cables within the bowden tubes may snap under high loads or after prolonged usage (due to wear and tear). Generally these instances will not result in user harm as the surrounding hardware/bowden tubes usually absorb the loads. There is a possibility that cuts or other sources of injury could occur in these scenarios (although across years of bowden-transmission usage we have never had an injury). We recommend performing frequent maintenance on bowden-cable based configurations and exercising caution when applying high torques (25+ Nm). We recommend using thicker steel cables (see recommendation in “Bowden Transmission” section) when expecting prolonged periods of high torque application. In instances where the steel cables do snap, remain calm and turn off the power to the system as early as possible.

## Pinch

The moving parts of the exoskeleton can cause pinches if care is not taken. For the hip configuration, users should never place their hands between the motors and uprights during use. For bowden cable configurations, users should never place fingers inside the cartridge or between the bowden cables. Moreover, users should avoid placing their hands between the hinges connecting the motors to the belt. In general, users should be aware of which parts of the exoskeleton articulate and keep appendages away from those areas.

## Blunt Force

The uprights attached to the motors can pose a significant risk if not securely fastened during operation. Due to their lightweight design, the motors can cause the uprights to spin rapidly if left unsecured (e.g., not attached to the thigh or calf via cuffs). To prevent injury, ensure the uprights are firmly attached to the user’s legs and never operate the exoskeleton if the uprights are unrestrained.

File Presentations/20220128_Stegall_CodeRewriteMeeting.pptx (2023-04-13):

## Code Rewrite

## Goals

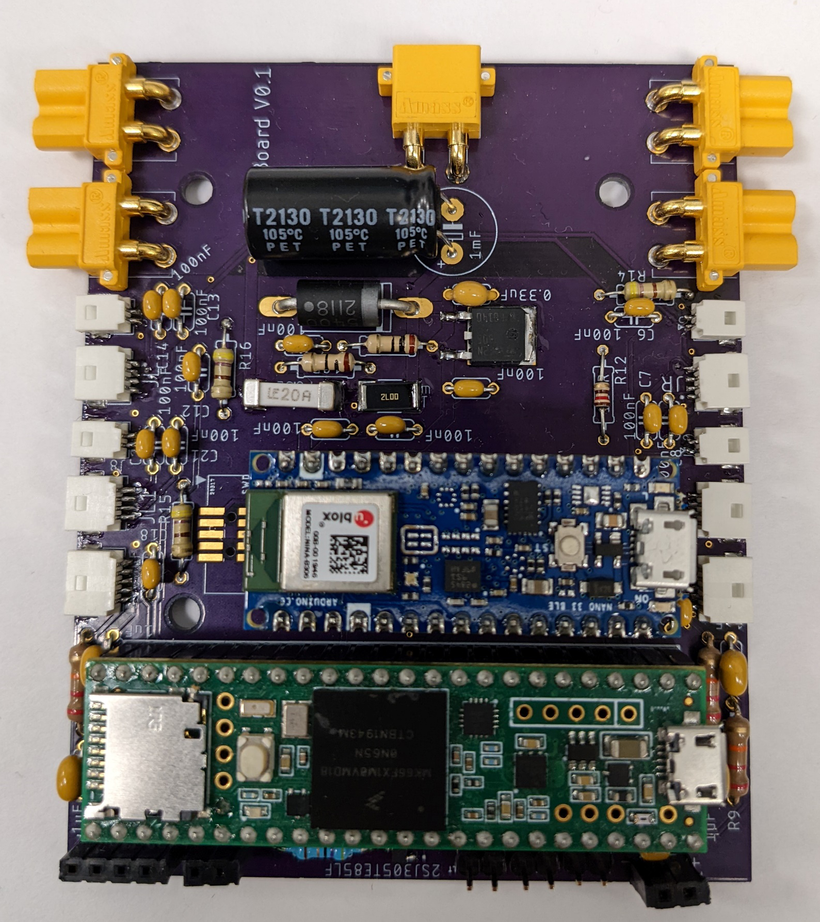
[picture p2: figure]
Picture of the dual microcontroller board

- Separate Bluetooth communication from exo control
  - Have nano for COMs and Teensy for control
- Prevent need to reflash boards when switching systems
  - Use SD card with config file
  - Have single file that compiles for both boards with preprocessor directives
- Update for use with CAN motors
- Make code more modular and flexible
  - Use object-oriented programing

## System Structure

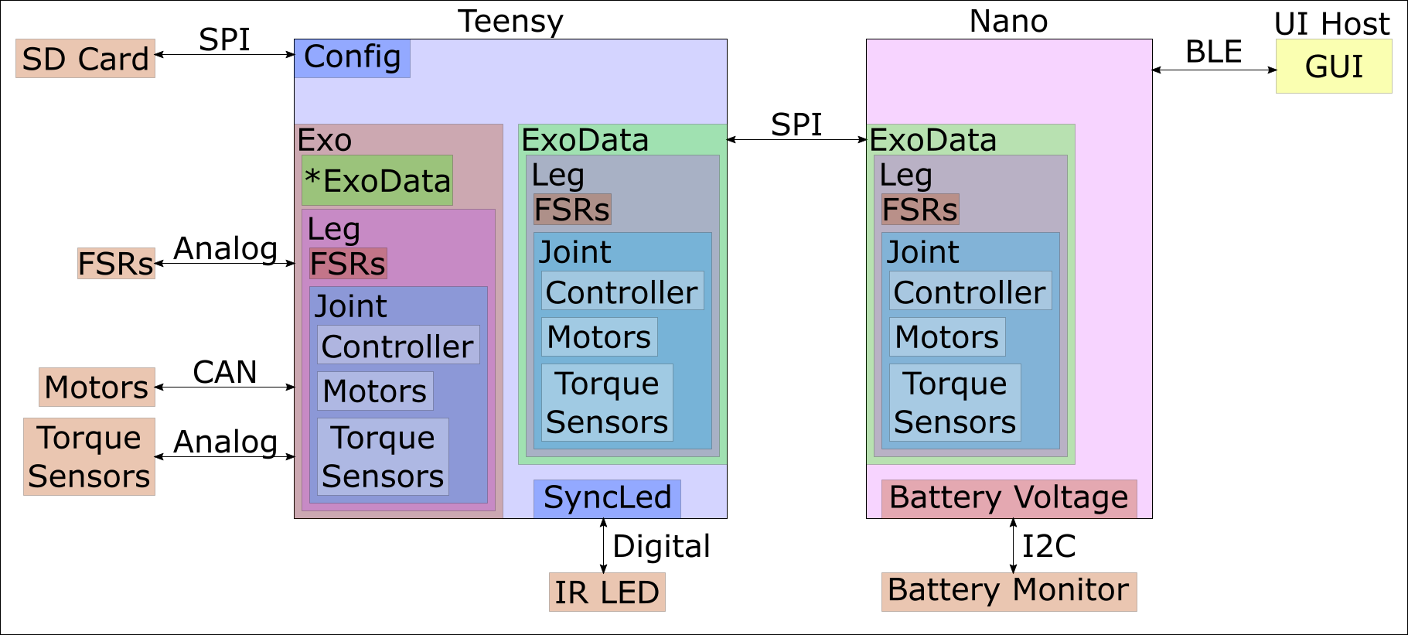
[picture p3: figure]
Code Diagram

## Concept of Operations

1. Check/update configuration on the SD Card
2. Turn on
3. Teensy reads config
  1. Sends info to Nano
4. Both boards create ExoData object
5. Teensy creates Exo object
6. Calibrates sensors
7. Select controllers to use for the joints
8. Start trial
  1. Teensy pulls updates from Nano
  2. Teensy reads data from sensors
  3. Teensy updates motor commands/Sync Led
  4. Teensy pushes data to Nano
9. End Trial

## Current Status

- Done
  - Config file reading done
  - ExoData structure in place and compiles on both boards
- Partially Done
  - Exo structure in place but needs functions filled in
  - LED objects work but need to be update to new style guide
- To Do
  - Board to board COMs
  - Nano to UI COMs
  - Battery Monitor

## Next Steps

- Fill in Functions
  - Start with external interfaces and work in from there.

## Open Questions

- Anything missing or needs changed in the style guide?
- Other things we should consider in the rewrite?
- SPI protocol data as large chunk or just read specific updates.

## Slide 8

ExoData
{
ExoStatus
sync_led_state
LegData : left, right
{
percent_gait
heel_fsr
toe_fsr
is_left
is_used
JointData : hip, knee, ankle
{
id
torque_reading
is_left
is_used
motor
{
id
motor_type
is_left
p
v
i
p_des
v_des
kp
kd
t_ff
}
controller
{
controller
JointType
setpoint
parameter1
parameter2
}
}
}
}

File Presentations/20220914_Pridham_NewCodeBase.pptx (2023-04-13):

## New Code Base

Paul Pridham
9/14/2022

## Why New Code?

- Nano:
  - Pro: has built in Bluetooth
  - Con: Slow clock
  - Con: Noisy ADC
- Teensy:
  - Pro: Fast Clock
  - Pro: Good ADC
  - Con: Needs external Bluetooth that can cause controls to hang while message is being sent
- Each controllers’ cons are not an issue with the other so by having the Teensy offload Bluetooth communication to the Nano we should end up with an overall faster system
- Expected possible control loop speed is ~600µs for 4 motors using 2 CAN busses and custom libraries.

## Overview

## UI Host

- Interface the user touches, app on phone or tablet
- Packages and sends individual Bluetooth messages.

## Nano

- Handles Bluetooth communication
- Mirrors ExoData stored on the Teensy
- Handles low frequency sensor reading

## Teensy

- Handles most of the computation
- Configures System
- Does primary sensor readings
  - FSR
  - Torque Sensors
- Does primary output
  - Motors
  - Sync LED
  - Status LED

## ExoData

- Stores the data and parameters used to control the system
- Mirrors setup of Exo

## Exo

- Handles the computation
- Reads sensors and puts data in ExoData instance.
  - FSR
  - Torque Sensors
- Calculates output commands and sends to components
  - Motors
  - Sync LED
  - Status LED

## SD Card

- Stores system configuration
- Till app fully set up:
  - Contains parameter sets for different controllers.

## Motors

- Currently CAN motors but other types can be added
- Takes in torque commands

## Torque Sensors

- Measures torques at the joint
- Controllers have flag to use PID
  - Select if torque sensor present
  - Don’t use if there is no torque sensor

## FSR

- Used to determine pressure at the heel and toe.
- Used to determine foot strike and percent gait based on that.
- Some controllers use one or both of these sensors.

## Status LED

- Displays messages based on exoskeleton status.
  - Colors (RGB)
  - Patterns
    - Solid (Color)
    - Blink (Color, Freq)
    - Pulse (Color, Freq)
    - Rainbow (Freq)

## Sync LED

- Used to synchronize the exoskeleton with infrared(IR) motion capture through an IR LED
- Pulse Pattern
  - Long pulse at start and end
  - Small pulses in middle

## Concept of Operations

1. Check/update configuration on the SD Card
2. Turn on
3. Teensy reads config
  1. Sends info to Nano
4. Both boards create ExoData object
5. Teensy creates Exo object
6. Calibrates sensors
7. Select controllers to use for the joints
8. Start trial
9. End trial

100 Hz*
  1. Teensy pulls updated app info from Nano
  2. Teensy pushes data to Nano
  3. Nano updates app

* These loops happen regardless of trial state

500+ Hz*
  1. Teensy reads data from sensors
  2. Teensy updates motor commands/Sync Led

## Concept of Operations

1. Check/update configuration on the SD Card
2. Turn on
3. Teensy reads config
  1. Sends info to Nano
4. Both boards create ExoData object
5. Teensy creates Exo object
6. Calibrates sensors
7. Select controllers to use for the joints
8. Start trial
9. End trial

100 Hz*
  1. Teensy pulls updated app info from Nano
  2. Teensy pushes data to Nano
  3. Nano updates app

* These loops happen regardless of trial state

500+ Hz*
  1. Teensy reads data from sensors
  2. Teensy updates motor commands/Sync Led

## Concept of Operations

1. Check/update configuration on the SD Card
2. Turn on
3. Teensy reads config
  1. Sends info to Nano
4. Both boards create ExoData object
5. Teensy creates Exo object
6. Calibrates sensors
7. Select controllers to use for the joints
8. Start trial
9. End trial

100 Hz*
  1. Teensy pulls updated app info from Nano
  2. Teensy pushes data to Nano
  3. Nano updates app

* These loops happen regardless of trial state

500+ Hz*
  1. Teensy reads data from sensors
  2. Teensy updates motor commands/Sync Led

## Concept of Operations

1. Check/update configuration on the SD Card
2. Turn on
3. Teensy reads config
  1. Sends info to Nano
4. Both boards create ExoData object
5. Teensy creates Exo object
6. Calibrates sensors
7. Select controllers to use for the joints
8. Start trial
9. End trial

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

* These loops happen regardless of trial state

500+ Hz*
  1. Teensy reads data from sensors
  2. Teensy updates motor commands/Sync Led

## Concept of Operations

1. Check/update configuration on the SD Card
2. Turn on
3. Teensy reads config
  1. Sends info to Nano
4. Both boards create ExoData object
5. Teensy creates Exo object
6. Calibrates sensors
7. Select controllers to use for the joints
8. Start trial
9. End trial

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

* These loops happen regardless of trial state

500+ Hz*
  1. Teensy reads data from sensors
  2. Teensy updates motor commands/Sync Led

## Concept of Operations

1. Check/update configuration on the SD Card
2. Turn on
3. Teensy reads config
  1. Sends info to Nano
4. Both boards create ExoData object
5. Teensy creates Exo object
6. Calibrates sensors
7. Select controllers to use for the joints
8. Start trial
9. End trial

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

* These loops happen regardless of trial state

500+ Hz*
  1. Teensy reads data from sensors
  2. Teensy updates motor commands/Sync Led

## Concept of Operations

1. Check/update configuration on the SD Card
2. Turn on
3. Teensy reads config
  1. Sends info to Nano
4. Both boards create ExoData object
5. Teensy creates Exo object
6. Calibrates sensors
7. Select controllers to use for the joints
8. Start trial
9. End trial

100 Hz*
  1. Nano pushes updated app info to the Teensy
  2. Nano pulls new sensor data from the Teensy
  3. Nano updates app

* These loops happen regardless of trial state

500+ Hz*
  1. Teensy reads data from sensors
  2. Teensy updates motor commands/Sync Led

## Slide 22

- Code Location
  - https://github.com/naubiomech/ExoCode/tree/nano_teensy_board
- User Guide
  - https://github.com/naubiomech/ExoCode/tree/nano_teensy_board/Documentation

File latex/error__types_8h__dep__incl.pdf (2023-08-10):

ExoCode/src/error_types.h

ExoCode/src/ComsMCU.cpp | ExoCode/src/ExoData.cpp | ExoCode/src/Motor.cpp

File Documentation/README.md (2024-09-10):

# User Guide

## Outline
1.  [Background](#background)
1.  [Introduction](#introduction)
    1. [Code location](#code-location)
    2. [Style Guide](#style-guide)
    3. [System Structure](#system-structure)
    4. [How to Deploy](#how-to-deploy)
2.  [High level functionality](#high-level-functionality)
    1. [Code Structure](#code-structure)
    2. [Guiding Principles](#guiding-principals)
    3. [Operation](#operation)
3.  [SD Card](#sd-card)
    1. [SD Configuration](#sd-configuration)
    2. [SD Controller Parameters](#sd-controller-parameters)
3.  [Sensors](#sensors)
    1. [Sensor Structure](#sensor-structure)
    2. [Adding New Sensors](#adding-new-sensors)
3.  [Displays](#displays)
    1. [Status LED](#status-led)
    2. [Sync LED](#sync-led)
4.  [Actuators](#actuators)
    1. [Actuator Structure](#actuator-structure)
    2. [Adding New Actuators](#adding-new-actuators)
    3. [T-motor Initialization](#t-motor-initialization) (Get info from Chance)
5.  [Controllers](#controllers)
    1. [Controller Structure](#controller-structure)
    2. [Adding New Controllers](#adding-new-controllers)
    3. [Controller Parameters](#controller-parameters)
6. [Bluetooth Communication](#bluetooth) (Get info from Chance)
    1. [Bluetooth Background](#bluetooth-background)
    2. [Bluetooth Structure](#bluetooth-structure)
    3. [Sending a Message](#sending-a-message)
7. [Debugging](#debug)
8. [Adding New](#adding-new)
    1. [Adding New Board](#adding-new-board)
    2. [Adding New Microcontroller](#adding-new-microcontroller)
    3. [Adding New Item To Config](#adding-new-item-to-config)
8. [Resources](#resources)
    1. [Lab Resources](#lab-resources)
    1. [C++ Resources](#c-resources)
    1. [Bluetooth Resources](#bluetooth-resources)
9. [Known Issues](#known-issues) 
**

## Background
The code is written in Arduino and C++.
This background section is intended to give you and understanding about the different things you may see in the code and how to interpret them.
More detailed information can be found on the internet, [tutorialspoint](https://www.tutorialspoint.com/cplusplus/index.htm) and [w3schools](https://www.w3schools.com/cpp/default.asp) are good but there are other resources that are as well.

### Bits and Bytes
A bit is the smallest unit of information that a computer can work with and store. It is represented by one of two states, either a 0 or a 1.

Bytes are composed of 8 bits and are typically the units used on a computer as a single bit is usually too small. One byte is usually capable of holding information for one character (e.g., 'D', 'o', 'g', '!') whereas 4 or 8 bytes are usually used to store intergers (e.g., 1, 4, 6, 8).

#### Bitwise Operators
& - bitwise AND; takes two bytes and performs AND on every bit. Will result in a 1 only if both bits are 1.

| - bitwise OR; takes two bytes and performs OR on every bit. Will result in a 1 if either of the two bits is a 1. 

**ex.** Simple Example
```
V0: 	0b10101010
V1: 	0b11110000
-------------------
V0 & V1:0b10100000
V0 | V1:0b11111010
```

#### Bit Shifting
Bit Shifting, as its name implies, moves the binary value of the bit of interest some determined number of places to the left or right. 
This is traditionally used for data storage purposes. For example, if you have a boolien (see section below) that will either have a 0 or a 1 it would be inefficient to store only that in a single byte. 
Thus, we can use bit shifting to store multiple booliens (e.g., 8) into a single byte, which is much more efficient. 

**ex.** [Utilities.cpp](/ExoCode/src/Utilities.cpp)
```
uint8_t update_bit(uint8_t original, bool val, uint8_t loc)
{
    uint8_t keep_bit = ~(1<<loc);  //set a mask for the bits we aren't setting 
    
    return (original & keep_bit) | (val<<loc);
};
```
1. This shifts a 1 into the loc position, so if loc is 2 it shifts the 1 two positions to the left 0b00000001<<2 becomes 0b00000100.
2. Then the ~ inverts the bits to: 0b11111011
3. Move the val to the current position val<<loc, for our 2 example this would put a 1 or 0 in the 2nd position with zeros for everything else.
4. original & keep_bit, keep_bit is the value from step 1, when added with the original it will return the original but with a 0 in the loc position
5. Or the values from 3 and 4, which will return the original with the bit in the loc position set to whatever was in val.

### Addresses
Data on the microcontroller are stored in a loctaion. The address represents the location that said data is stored. An example of what an address looks like would be: 0x7ffcccc2f420

### Variables
Variables are used as a means to store data/information. Variables have a name that pertains to its identity and helps distinguish it from other pieces of data/information.
When creating a variable you must declare (specify) its type. Information on types can be found in the section below.

**Syntax:** type variable_name = value;

**ex.** [BleMessage.h](/ExoCode/src/BleMessage.h)

```
// Number of parameters to expect with the command
int expecting = 0;
``` 

### Types
Data types specify the type of information that can be stored as well as the size of the information that can be stored. The types encountered in our code are as follows:

#### Bool
The Bool (Boolean) type can store true (1) or false (0) values.

**ex.** [ExoCode.ino](/ExoCode/ExoCode.ino)
```
static bool first_run = true;
```
This variable stores if it is the first run of the loop().
If it is we do some startup stuff, then change it to false.
A bool is still stored in a byte so it doesn't save a ton of room unless you pack a bunch of them into another type.

##### Logical Operators
&& - Logical AND; Returns "true" if both statements are true.

|| - Logical OR; Returns "true" if at least one statement is true.

!  - Logical NOT; Changes the result to its opposite (e.g., would display false if the result was true)

**ex.** Simple Example
```
bool dogs_are_cute = true;
bool cats_are_nice = false;
bool dogs_bark = true;

cout << dogs_are_cute && dogs_bark;  		//Would output true
cout << dogs_are_cute && cats_are_nice; 	//Would output false

cout << dogs_are_cute || cats_are_nice;		//Would output true

cout << !(dogs_are_cute && cats_are_nice);	//Would output true
```

#### Char
The Char type can store one character. The character should be surrounded by single quotes (e.g., 'P','u','p','p','y').

**ex.** [BleMessage.h](/ExoCode/src/BleMessage.h)
```
// GUI command
char command = 0;
```

#### Int
The int type is used when storing numbers without a decimal. 

**ex.** [BleMessage.h](/ExoCode/src/BleMessage.h)
```
// Number of parameters to expect with the command
int expecting = 0;
```

#### Float
The float type is used when storing numbers that have a decimal. It is capable of occupying 32 bits which is approximately 7 decimal places.

**ex.** [TorqueSensor.h](/ExoCode/src/TorqueSensor.h)
```
float _calibrated_reading;
```

#### Double
A double also stores numbers that have a decimal place but has double the precision of the float (hence the name). That is, it can occupy 64 bits which is approximately 15 decimal places. 

**ex.** We don't really use doubles but it is here for completeness.

#### Arrays
Arrays are used to store several values witin one variable. Similar to other variables, arrays need a data type (e.g., int, bool, float...). 
Each value in the array is called an element which has its own index (place within the array). It should be noted that the indexing starts at 0 rather than 1. So to access the first element in the array you would use index 0.

**Syntax:** type name[number_of_elements] = {element1, element2, ....};

**ex.** Simple Example

```
int numbers [6] = {10, 20, 30, 40, 50, 60};

cout << numbers[0];	//Would output 10
cout << numbers[1];	//Would output 20
```

**ex.** [ExoCode.ino](/ExoCode/ExoCode.ino)
```
uint8_t (config_to_send)[ini_config::number_of_keys];
```

#### Void
Void means that there is no type, thus variables cannot be defined with "void".
The primary utilization of void is for functions that return no values (more on those later).

**ex.** [SyncLed.cpp](/ExoCode/src/SyncLed.cpp)
```
/*
* Sets the flags to start or stop the blink sequence
*/
void SyncLed::trigger()
{
	_do_start_stop_sequence = _do_start_stop_sequence ^ true;  // xor with one to change boolean state
	_do_blink = _do_blink ^ true;  // xor with one to change boolean state
	_state_change_count = 0;  // reset the state change count.
};
```

#### Typecasting
Typecasting converts a variable of one type into a different type. There are two types of typecasting: Implicit and Explicit.

Implicit typecasting occurs when the compiler automatically converts one data type to another without explicit programmer intervention.

**ex.** Implicit Typecasting - Simple Example
```
int value = 40;
char letter = 'd';

int result = value + letter;

cout << result; //Prints out the value of result, which is 140
```

Explicit typecasting occurs when the programmer manually changes a variable from one data type to another. Format: (new type) variable;

**ex.** Explicit Typecasting - Simple Example
```
int value;
value = (int)12.2333;

cout << value; //Prints out the value, which is 12
```

**ex.** [Utilities.h](/ExoCode/src/Utilities.h)
```
val.i = (short int) (num_to_convert * factor);
```

#### Modifiers
Modifiers are used to alter the meaning of varilabe types (e.g., int, double, char) in order to better match the requirements of different circumstances.
There are 4 type modifiers in C++: Signed, Unsigned, Long, Short. It should be noted that you can use combination of modifyers (e.g., unsigned long int)

##### Signed vs Unsigned
Signed and unsigned modifiers can only be used with int and char data types.

Signed variables are capable of storing postitive and negative values as well as zero. The type int by defult is signed. (Signed Int Value Range: -2,147,483,648 to 2,147,483,647)

Unsigned variables are only capable of storing postive values and zero. These can never be negative. (Unsigned Int Value Range: 0 to 4,294,967,295)

Signed variables use one extra bit to account for the sign of the value (compared to unsigned), hence unsigned can be used to save extra space. 

**ex.** [BleParser.cpp](/ExoCode/src/BleParser.cpp)
```
//Get the amount of characters to wait for
for(unsigned int i=0; i < sizeof(ble::commands)/sizeof(ble::commands[0]); i++)
{
```

##### Long and Short
The long modifier modifies the maximum value that a data type can hold. Long can be used for int and double data types. Long modifiers can be used twice (int only) to create larger numbers (e.g., long long int). 

The short modifier modifies the minimum value that a data type can hold. Short can be used for int.

The primary value of using these modifiers is for memory usage purposes. A short int will use less bytes than an int whereas a long int will use more bytes than an int. 

**ex.** [Utilities.h](/ExoCode/src/Utilities.h)
```
val.i = (short int) (num_to_convert * factor);
```

##### Static
A static variable means that the variable is created at the start of the program and destroyed at the end of the program. This allows the variable to maintain its value even after going beyond its scope.

Scope helps determine where the variable can be accessed within the code. There are generally two types: Local and Global. 

Local Scope: variables can only be accessed within the block of code that they are declared. 

Global Scope: variables can be access from the time of declaration within the code until the end of the code. 

**ex.** [ExoCode.ino](/ExoCode/ExoCode.ino)
```
static bool first_run = true;
```

##### Volatile
A volatile variable means that the value may change between accesses to the variable, even if said variable appears unmodified. The use of volatile guarantees that the varilabe will be read again before any usage. 
This may be useful in a situation when a controller may try to use a previous copy of the variable value (that it assumes are unchanged) rather than reading and writing using the current value. 
This is common in situations when the variable value can change due to something outside of the code (e.g., hardware that changes the value).

**ex.** [SyncLed.h](/ExoCode/src/SyncLed.h)
```
volatile int _current_sync_period; // The current period to use.  Whenever syncLedHandler is called the interupt should have another begin call to make sure the period is correct.
```

##### Extern

Extern is useful when using multiple modules. You can define a variable in one .cpp file and then use that variable in another .cpp file without defining it.

**ex.** Simple Example

FileOne.cpp

```
int variable = 20;
```

FileTwo.cpp
```
extern int variable;
cout << variable; //This would output 20
```

**ex.** [SPIHandler.h](/ExoCode/src/SPIHandler.h)
```
extern uint8_t is_ff[num_bytes];
```

### Conditions
Expressions within the code that will be either true or false. 
Typically the outcome of these conditions will determine how/if certain sections of code are run.

#### If-Else Statments
If statements specify a section of code that will run if the condition is evaluated as true.
Else statments specify a section of code that will run if the condition is evaluated as false. Else statments are not required (that is, you do not need to have a section of code that runs if the condition is evaluated as false).
It is possible to have multiple conditions, in which case we can use "else if" statements as part of the evaluation. 

**Syntax:**
```
if (condition_one)
{
	//Code to run if true
}
else if (condition_two)
{
	//Code to run if true
}
else
{
	//Code to run 
}
```

**ex.** Simple Example
```
int x = 20;
int y = 42;

if (x < y)
{
	cout << "The dog is really really good.";
}
else if (x > y)
{
	cout << "The dog is really good."
}
else
{
	cout << "The dog is good."
}
```

There is an alternative way to formulate if-else statments within the code that signficantly reduces the amount of space used by these statments.
Note that this only works if there is one condition to be evaluated (does not work for "else if").
This formulation is commonly used throughout our code. 

**Syntax:** variable = (condition) ? if_true : if_false;

**ex.** Simple Example
```
int x = 20;
int y = 42;

string result = (x < y) ? "The dog is really really good." : "The dog is really good."
cout << result;
```

**ex.** [Controller.cpp](/ExoCode/src/Controller.cpp)
```
float ZeroTorque::calc_motor_cmd()
{
    float cmd_ff = 0;
    
    // add the PID contribution to the feed forward command
    float cmd = cmd_ff + (_controller_data->parameters[controller_defs::zero_torque::use_pid_idx] 
                ? _pid(cmd_ff, _joint_data->torque_reading,_controller_data->parameters[controller_defs::zero_torque::p_gain_idx], _controller_data->parameters[controller_defs::zero_torque::i_gain_idx], _controller_data->parameters[controller_defs::zero_torque::d_gain_idx]) 
                : 0);
   
    return cmd;
};
```

In the above example, the condition being evaluated is whether or not we are using PID control and if it is true then it augments the feed forward command appropriately. 

#### Switch Statements
Switch statements are valuable when there are several different blocks of code that could be run depending on if an expression is true.

**Syntax:**
```
switch(expression)
{
	case x:
		//Code to be run
	   break;
	case y:
		//Code to be run
	   break;
	case z:
		//Code to be run
	   break;
	default:
		//Code to be run
}
```

If the expression matches the case value (x, y, z in the above syntax), then the block of code for that case runs. 
The code will run until it reaches the "break" keyword, this is useful as this will cause the code to skip the rest of the switch blocks which can save considerable time. 
In some instances it is useful to have a section of code that runs if the expression does not match any of the cases. This is where the "default" keyword comes into use. 
Importantly, this default must be the last statment used (no break is required). Also note that the expression used in these statments must be of type int or enum.

**ex.** Simple Example
```
int month = 5;

switch (month)
{
	case 1:
		cout << "January";
	   break;
	case 2:
		cout << "February";
	   break;
	case 3:
		cout << "March";
	   break;
	case 4:
		cout << "April";
	   break;
	case 5:
		cout << "May";
	   break;
	case 6:
		cout << "June";
	   break;
	case 7:
		cout << "July";
	   break;
	case 8:
		cout << "August";
	   break;
	case 9:
		cout << "September";
	   break;
	case 10:
		cout << "October";
	   break;
	case 11:
		cout << "November";
	   break;
	case 12:
		cout << "December";
	   break;
	default:
		cout << "This is not a month.";
}

```

**ex.** [Controller.cpp](/ExoCode/src/Controller.cpp)
```
 switch (utils::get_joint_type(_id))
    {
        case (uint8_t)config_defs::joint_id::hip:
            #ifdef CONTROLLER_DEBUG
                logger::print("HIP ");
            #endif
            if (is_left)
            {
                _controller_data = &(exo_data->left_side.hip.controller);
                _joint_data = &(exo_data->left_side.hip);
            }
            else
            {
                _controller_data = &(exo_data->right_side.hip.controller);
                _joint_data = &(exo_data->right_side.hip);
            }
            break;
            
        case (uint8_t)config_defs::joint_id::knee:
            #ifdef CONTROLLER_DEBUG
                logger::print("KNEE ");
            #endif
            if (is_left)
            {
                _controller_data = &(exo_data->left_side.knee.controller);
                _joint_data = &(exo_data->left_side.knee);
            }
            else
            {
                _controller_data = &(exo_data->right_side.knee.controller);
                _joint_data = &(exo_data->right_side.knee);
            }
            break;
        
        case (uint8_t)config_defs::joint_id::ankle:
            #ifdef CONTROLLER_DEBUG
                logger::print("ANKLE ");
            #endif
            if (is_left)
            {
                _controller_data = &(exo_data->left_side.ankle.controller);
                _joint_data = &(exo_data->left_side.ankle);
            }
            else
            {
                _controller_data = &(exo_data->right_side.ankle.controller);
                _joint_data = &(exo_data->right_side.ankle);
            }
            break;
        case (uint8_t)config_defs::joint_id::elbow:
            #ifdef CONTROLLER_DEBUG
                        logger::print("ELBOW ");
            #endif
            if (is_left)
            {
                _controller_data = &(exo_data->left_side.elbow.controller);
                _joint_data = &(exo_data->left_side.elbow);
            }
            else
            {
                _controller_data = &(exo_data->right_side.elbow.controller);
                _joint_data = &(exo_data->right_side.elbow);
            }
            break;
    }
```

### Functions
Functions, sometimes refered to as methods or procdures, are a reusable block of code designed to do a particular task. 
Functions allow for code to be split into smaller, modular pieces and are particularly useful when sets of code need to be used several times. 

There are typically two parts to creating a function:

Declaration - tells the code's compiler what the functions name, return type, and parameters are

Definintion - the main body of the function, the instructions for what the function does

**Syntax:**
```
return_type function_name(parameters) //Declaration
{
	//Definition
}
```

If the function has a return, the return will be the last line of code within the block that executes, even if there are lines after it. 

**ex.** Simple Example
```
int square(int x)
{
	return x*x;
}

int main()
{
	int result = square(2);
	cout << result; 			//Will output 4
}
```

**ex.** [Utilities.cpp](/ExoCode/src/Utilities.cpp)
```
bool get_is_left(uint8_t id)
{
    return (id & (uint8_t)config_defs::joint_id::left) == (uint8_t)config_defs::joint_id::left;
};
```

#### Overloading
Function overloading is when there are multiple functions of the same name but with different parameters. These differences in parameters could manifest as type differences, number of parameters in the function, or as both.
Overloading is useful when you have multiple functions that do the same thing. 

**ex.** Simple Example
```
int multiply(int x, int y)
{
	return x*y;
}

double multiply(double x, double y)
{
	return x*y;
}

int multiply (int x, int y, int z)
{
	return x*y*z;
}

int main()
{
	cout << multiply(2,3) << "\n"; 		//Outputs a value of 6
	cout << multiply(2.5,3.2) << "\n"; 	//Outputs a value of 8.0
	cout << multiply(2,3,4) << "\n";	//Outputs a value of 24
}
```

**ex.** [Utilities.cpp](/ExoCode/src/Utilities.cpp)
```
/*
 * From the joint_id returns the bit for is_left.
 */
bool get_is_left(config_defs::joint_id id)
{
    return get_is_left((uint8_t) id);//((uint8_t)id & (uint8_t)config_defs::joint_id::left) == (uint8_t)config_defs::joint_id::left;
};
bool get_is_left(uint8_t id)
{
    return (id & (uint8_t)config_defs::joint_id::left) == (uint8_t)config_defs::joint_id::left;
};
```

### Classes
Classes are user defined data types. Objects are instanaces of the class.
Classes are the template/blueprint for the object, where as the object gets its characteristics and behaviors from the class. 
A class can contain both attributes (variables) and methods (functions). Both of these are usually referred to as members of the class. 

**Syntax:**
```
class Class_Name
{
	//Specifiers_Attributes_and_Methods
};
```

**Note:** After the final bracket of a class, you must place a ';'

Similar to functions, classes need to be declared and defined. These are usually done separately with the declaration occuring in a header file (.h, more on that later) and the definition occuring within a .cpp file.

To create an object of a class you need to use the following synatx: class_name object_name;

To assign attributes to an object or utilize a method for an object, use the following syntax: object_name.attribute_or_method_name; 

**ex.** Simple Example
```
class Dogs
{
	public:
	string name; 	//The Dog's Name
	string breed; 	//The Dog's Breed
	int age;		//The Dog's Age
	
	void dog_information()
	{
		cout << name << " is a " << age << " year old " << breed << "\n";
	}
};

int main()
{
	Dogs dog1;		//Creates an object of Dogs
	dog1.name = "Mr.Pebbles";		//Assigns a value to the name attribute 
	dog1.breed = "Golden Retriever";		//Assigns a value to the breed attribute
	dog1.age = 4;		//Assigns a value to the age attribute 
	
	dog1.dog_information();		//Utilizes the class's method to output "Mr. Pebbles is a 4 year old Golden Retriever"
}	
```
You may have noticed the word "public" in the above example. This is an instance of a classes' access specifier. Specifiers determine how attributes and methods of a class can be accessed.
Generally, there are three types:

Public - attributes and methods accessible outside of the class.

Private - attributes and methods are not accessible outside of the class. (private is the defult specification for members of a class).

Protected - attributes and methods are not accessible outside of the class but can be accessed via inherited classes (more on those later).

While some functions are definied within the class itself, such as above, there is also a way to define a funciton for a class outside of the class itself.
To do so, you need to utilize the scope resolution operator: "::". It should be noted while the function can be defined outside of the class it still must be declared within it. 

**Syntax**
```
class class_name
{
	//Attributes
	type function_name(parameters); //You still must declare the function within the class
};

type function_name(parameters)
{
	//Block of Code
}
```

**ex.** Simple Example
```
class Dogs
{
	public:
	string name; 	//The Dog's Name
	string breed; 	//The Dog's Breed
	int age;		//The Dog's Age
	
	void dog_information(); //Method Declaration
};

void Dog::dog_information()
	{
		cout << name << " is a " << age << " year old " << breed << "\n";
	}

int main()
{
	Dogs dog1; 							//Creates an object of Dogs
	dog1.name = "Mr.Pebbles";			//Assigns a value to the name attribute 
	dog1.breed = "Golden Retriever";	//Assigns a value to the breed attribute
	dog1.age = 4;						//Assigns a value to the age attribute 
	
	dog1.dog_information();		//Utilizes the class's method to output "Mr. Pebbles is a 4 year old Golden Retriever"
}	
```

**ex.** [Controller.h](/ExoCode/src/Controller.h)
```
class ProportionalJointMoment : public _Controller
{
    public:
        ProportionalJointMoment(config_defs::joint_id id, ExoData* exo_data);
        ~ProportionalJointMoment(){};

        float calc_motor_cmd();
};
```

#### Constructor
Constructors are a method within a class that is automatically called upon creation of an object. 
The primary purpose of a constructor is to initialize members of the object with data. It makes sure that an object is created with specific attributes. 
Constructors construct the values of the objects (hence it's name). These methods have no return value (thus they do not have a return type).

Note: Constructors must have the same name as the class and all members within a constructor are public. 

**ex.** [Controller.h](/ExoCode/src/Controller.h)
```
class ProportionalJointMoment : public _Controller
{
    public:
        ProportionalJointMoment(config_defs::joint_id id, ExoData* exo_data); //This is the constructor
        ~ProportionalJointMoment(){};

        float calc_motor_cmd();
};
```

#### Inheritance
Inheritance is when a class (called a child, derived, or sub class) takes (inherits, hence the name) attributes and methods from another class (called a partent, base, or super class).
Typically this new class then extends upon the inherited members of the parent class through new attributes and/or methods.
This can be used in a modular sense to considerablly reduce the amount of potentially redundent code within a program.
It is possible to inherit from a class which itself inherited from another class. This can allow us to start with a very general class that then becomes progressivly more specific with each instance of inheritance.

**Syntax:**
```
Class Child: Class Parent
{
	//Code_Block
};
```

**ex.** Simple Example

```
Class Person				//Parent Class
{
	public:
	string name;
	int age;
	int height;
	int weight;
};

Class Football_Player : Person		//Child Class inheriting from Parent Class
{
	public:
	int pass_yards;
	int rushing_yards;
	int sacks;
	int interceptions;
};
```

**ex.** [Controller.h](/ExoCode/src/Controller.h)
```
class ProportionalJointMoment : public _Controller
{
    public:
        ProportionalJointMoment(config_defs::joint_id id, ExoData* exo_data);
        ~ProportionalJointMoment(){};

        float calc_motor_cmd();
};
```

In the above example we have a specific controller class (ProportionalJointMoment) inherit members from a more generic controller class (_Controller).

More info on inheritance can be found on [tutorialspoint](https://www.tutorialspoint.com/cplusplus/cpp_inheritance.htm) or [w3schools](https://www.w3schools.com/cpp/cpp_inheritance.asp).

#### Friend Classes
Friend classes can access private/protected memebers of other classes. 

**Syntax:** friend class name_of_class_you_want_to_befriend;

**ex.** We don't really use friend classes but it is here for completeness.

#### Abstract Classes
Abstact classess (also called interfaces) provide a base class from which other classes can inherit. These classes can not be used to create objects, they only serve as an interface.
A class is made abstract when at least one of its functions is made to be a pure virtual function (syntax: virtual type function_name(parameters) = 0;). 

**ex.** [Controller.h](/ExoCode/src/Controller.h)
```
class _Controller
{
	public:
        /**
         * @brief Constructor 
         * 
         * @param id of the joint being used
         * @param pointer to the full ExoData instance
         */
        _Controller(config_defs::joint_id id, ExoData* exo_data);
		
        /**
         * @brief Virtual destructor is needed to make sure the correct destructor is called when the derived class is deleted.
         */
        virtual ~_Controller(){};
        
        /**
         * @brief Virtual function so that each controller must create a function that will calculate the motor command
         * 
         * @return Torque in Nm.
         */
		virtual float calc_motor_cmd() = 0; 
        
        /**
         * @brief Resets the integral sum for the controller
         */
        void reset_integral(); 
        
    protected:
        
        ExoData* _data;                     /**< Pointer to the full data instance*/
        ControllerData* _controller_data;   /**< Pointer to the data associated with this controller */
        SideData* _side_data;                 /**< Pointer for the side data the controller is associated with */
        JointData* _joint_data;             /**< Pointer to the joint data the controller is associated with */
         
        config_defs::joint_id _id;          /**< Id of the joint this controller is attached to. */
        
        Time_Helper* _t_helper;             /**< Instance of the time helper to track when things happen used to check if we have a set time for the PID */
        float _t_helper_context;            /**< Store the context for the timer helper */
        float _t_helper_delta_t;            /**< Time time since the last event */

        //Values for the PID controller
        float _pid_error_sum = 0;           /**< Summed error term for calucating intergral term */
        float _prev_input;                  /**< Prev error term for calculating derivative */
        float _prev_de_dt;                  /**< Prev error derivative used if the timestep is not good*/
        float _prev_pid_time;               /**< Prev time the PID was called */
        
        /**
         * @brief calculates the current PID contribution to the motor command. 
         * 
         * @param controller command 
         * @param measured controlled value
         * @param proportional gain
         * @param integral gain
         * @param derivative gain
         */
        float _pid(float cmd, float measurement, float p_gain, float i_gain, float d_gain);
        
        //Values for the Compact Form Model Free Adaptive Controller
        std::pair<float, float> measurements;
        std::pair<float, float> outputs;
        std::pair<float, float> phi;            /**< Psuedo partial derivative */
        float rho;                              /**< Penalty factor (0,1) */
        float lamda;                            /**< Weighting factor limits delta u */
        float etta;                             /**< Step size constant (0, 1] */
        float mu;                               /**< Weighting factor that limits the variance of u */
        float upsilon;                          /**< A sufficiently small integer ~10^-5 */
        float phi_1;                            /**< Initial/reset condition for estimation of psuedo partial derivitave */
        
        float _cf_mfac(float reference, float current_measurement);
};
```

#### Initializer List
Initializer lists are used to initializing members of classes with data. 

**Syntax:**
constructor(parameters): initializaiton

**ex.** Simple Example
```
Class Example
{
	private:
		int number;
	public:
		Example(int number):number(5) {}
};
		
```

**ex.** [Controller.cpp](/ExoCode/src/Controller.cpp)
```
ZeroTorque::ZeroTorque(config_defs::joint_id id, ExoData* exo_data)
: _Controller(id, exo_data)
{
    
    #ifdef CONTROLLER_DEBUG
        logger::println("ZeroTorque::Constructor");
    #endif
    
};
```

### Pointers
Pointers are variables that contain the memory address as a value.
These variables point to a data type of the same type. 

**Synatx:** type* variable_name or type *variable_name   

**ex.** [Joint.h](/ExoCode/src/Joint.h)
```
_Motor* _motor; // using pointer to the base class so we can use any motor type.
JointData* _joint_data;
```

To get the address of a varilable, you can use "&" in front of the variable. 

**ex.** Simple Example
```
int age = 34;

int* pointer = &age;

cout << pointer; //outputs the address stored in the pointer 
```

You can also do the opposite and get the value of a variable from it's memory address through a technique called dereferencing. 

**Syntax:** *pointer

**ex.** Simple Example
```
int age = 34;

int* pointer = &age;

cout << pointer; 			//Outputs the address stored in the pointer 

cout << "\n" << *pointer; 	//Outputs the value of the variable at the location given by the pointer (aka age)
```

Within the code you may run into "->". This is used with pointers and is equivalent to using "object.attribute" within classes. 

**ex.** [Controller.cpp](/ExoCode/src/Controller.cpp)
```
    if (is_left)
    {
        _side_data = &(exo_data->left_side);
    }
    else
    {
        _side_data = &(exo_data->right_side);
    } 
```

#### Function Pointers
Function pointers are similar to regular pointers except that they store the address to functions rather than variables. 
These can be used to call a function indirectly. 

**Syntax:** type (*function_pointer)(argument);

These can also be initialized via the following synatx: type (*function_pointer)(argument){&function};

**ex.** Simple Example
```
int multiply(int x, int y)
{
	return x*y;
}

int main()
{
	int (*Function_Pointer)(int,int);   		//Declares function pointer
	Function_Pointer = multiply;				//Points to the function
	int result = Function_Pointer(4,3);			//Uses the function pointer to call a function indirectly
	int result2 = (*Function_Pointer)(4,3); 	//Another way to use the function pointer to call a function indirectly (will output the same result as above)
	cout << result;								//Outputs the result
}
```

**ex.** [ExoData.h](/ExoCode/src/ExoData.h)
```
// Type used for the for each joint method, the function should take JointData as input and return void
typedef void (*for_each_joint_function_t) (JointData*);
```

One other useful feature of function pointers is that they can be used as an argument to another function.
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

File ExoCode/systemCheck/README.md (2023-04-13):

# System Check
## Purpose
This folder is intended to provide tools for checking the function of individual components of the system.

## Use
There are different Arduino sketch folders for the different system checks.
If you are using the sketches you will need to copy the src folder from the main ExoCode here to make sure you have the most recent copy.
DO NOT commit these src subfolders, the .gitignore should take care of it but just to be safe.

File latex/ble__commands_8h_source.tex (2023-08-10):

\doxysection{ble\+\_\+commands.\+h}
\hypertarget{ble__commands_8h_source}{}\label{ble__commands_8h_source}\index{ExoCode/src/ble\_commands.h@{ExoCode/src/ble\_commands.h}}
\mbox{\hyperlink{ble__commands_8h}{Go to the documentation of this file.}}
\begin{DoxyCode}{0}
\DoxyCodeLine{00001\ }
\DoxyCodeLine{00009\ \textcolor{preprocessor}{\#ifndef\ BLE\_COMMANDS\_H}}
\DoxyCodeLine{00010\ \textcolor{preprocessor}{\#define\ BLE\_COMMANDS\_H}}
\DoxyCodeLine{00011\ }
\DoxyCodeLine{00012\ \textcolor{preprocessor}{\#include\ "{}Arduino.h"{}}}
\DoxyCodeLine{00013\ \textcolor{preprocessor}{\#include\ "{}\mbox{\hyperlink{_exo_data_8h}{ExoData.h}}"{}}}
\DoxyCodeLine{00014\ \textcolor{preprocessor}{\#include\ "{}\mbox{\hyperlink{_parse_ini_8h}{ParseIni.h}}"{}}\ \textcolor{comment}{//\ For\ config\_defs}}
\DoxyCodeLine{00015\ \textcolor{preprocessor}{\#include\ "{}\mbox{\hyperlink{_status_defs_8h}{StatusDefs.h}}"{}}\ \textcolor{comment}{//\ For\ ExoDataStatus\_t}}
\DoxyCodeLine{00016\ \textcolor{preprocessor}{\#include\ "{}\mbox{\hyperlink{_ble_message_8h}{BleMessage.h}}"{}}}
\DoxyCodeLine{00017\ \textcolor{preprocessor}{\#include\ "{}\mbox{\hyperlink{_params_from_s_d_8h}{ParamsFromSD.h}}"{}}}
\DoxyCodeLine{00018\ }
\DoxyCodeLine{00019\ \textcolor{preprocessor}{\#include\ "{}\mbox{\hyperlink{_u_a_r_t_handler_8h}{UARTHandler.h}}"{}}}
\DoxyCodeLine{00020\ \textcolor{preprocessor}{\#include\ "{}\mbox{\hyperlink{uart__commands_8h}{uart\_commands.h}}"{}}}
\DoxyCodeLine{00021\ \textcolor{preprocessor}{\#include\ "{}\mbox{\hyperlink{_u_a_r_t__msg__t_8h}{UART\_msg\_t.h}}"{}}}
\DoxyCodeLine{00022\ \textcolor{preprocessor}{\#include\ "{}\mbox{\hyperlink{_logger_8h}{Logger.h}}"{}}}
\DoxyCodeLine{00023\ }
\DoxyCodeLine{00028\ \textcolor{keyword}{typedef}\ \textcolor{keyword}{struct}}
\DoxyCodeLine{00029\ \{}
\DoxyCodeLine{00030\ \ \ \ \ \textcolor{keywordtype}{char}\ \mbox{\hyperlink{structble__command__t_a27bc785d9b070a90b7dce7eb9bd7e2a5}{command}};}
\DoxyCodeLine{00031\ \ \ \ \ \textcolor{keywordtype}{int}\ \mbox{\hyperlink{structble__command__t_a9c35a6470f545b930267235f8e2e60da}{length}};\ }
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

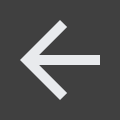
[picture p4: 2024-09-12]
Python_GUI/Resources/Images/ArrowBack.png

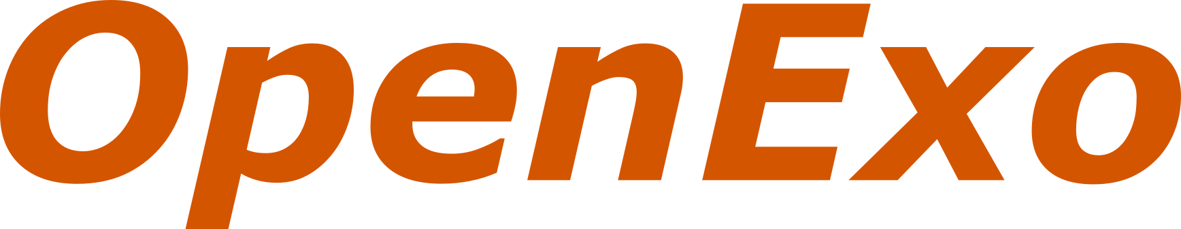
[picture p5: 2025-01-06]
Python_GUI/Resources/Images/OpenExo.png

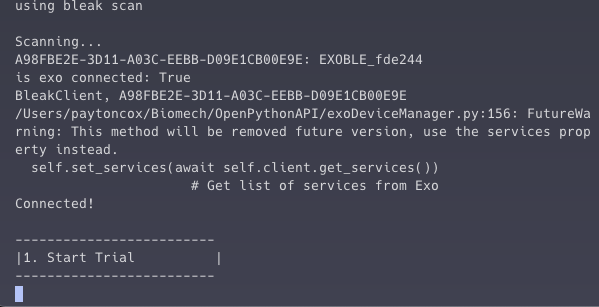
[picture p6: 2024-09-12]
Python_GUI/UI_Examples/Connected.png

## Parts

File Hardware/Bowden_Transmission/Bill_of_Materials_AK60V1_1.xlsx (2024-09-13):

Item | Link | Count | Price ($) | Total ($)
Machined Parts
Sprocket (x2) AND Cable - Chain Interface (x4) | https://www.hubs.com/ | 1 | 432.58 | 432.58
Prefabricated Parts
Chain Master Link | https://www.mcmaster.com/catalog/130/1314/6027K71 | 4 | 1.78 | 7.12
04B Chain (1ft) | https://www.mcmaster.com/catalog/130/1314/6027K71 | 1 | 9.02 | 9.02
TMotors AK60V1.1 KV80 | https://www.cubemars.com/goods-1142-AK60-6+V11+KV80.html | 2 | 298.9 | 597.8
6mm x 13mm x 5mm Flanged Ball Bearing (package of 10) | https://www.amazon.com/HiPicco-Flanged-Bearing-Shielded-Bearings/dp/B0CRLFPJPG?th=1 | 1 | 7.99 | 7.99
Steel Cable (500ft) | https://www.amazon.com/gp/product/B00TYSBDPU/ref=ppx_yo_dt_b_search_asin_title?ie=UTF8&psc=1 | 1 | 99 | 99
Cable Crimps (pack of 50) | https://www.mcmaster.com/catalog/130/1731/3914T11 | 1 | 9.04 | 9.04
Fasteners
M3X8 Buttonhead Screw (pack of 100) | https://www.mcmaster.com/products/screws/system-of-measurement~metric/rounded-head-screws~/metric-18-8-stainless-steel-button-head-hex-drive-screws/thread-siz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 | 1 | 8 | 8
M3X6 Buttonhead Screw (pack of 100) | https://www.mcmaster.com/products/screws/system-of-measurement~metric/rounded-head-screws~/metric-18-8-stainless-steel-button-head-hex-drive-screws/finish~pas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 | 1 | 5.83 | 5.83
M3X30 Flathead Screw (pack of 50) | https://www.mcmaster.com/products/screws/flat-head-screws~/metric-alloy-steel-hex-drive-flat-head-screws/thread-size~m3/length~30-mm/ | 1 | 6.93 | 6.93
M5X20 Buttonhead Screw (pack of 50) | https://www.mcmaster.com/products/screws/rounded-head-screws~/metric-18-8-stainless-steel-button-head-hex-drive-screws/thread-size~m5/length~20-mm/finish~pass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 | 1 | 12.38 | 12.38
M5 Lock Nuts (pack of 50) | https://www.mcmaster.com/products/nuts/locknuts~/nylon-insert-locknuts~~/system-of-measurement~metric/thread-size~m5/material~stainless-steel-2/ | 1 | 7.26 | 7.26
M3 Washer (pack of 10) | https://www.mcmaster.com/products/washers/washers-2~/metric-general-purpose-washers/screw-size~m3/material~aluminum-1/ | 1 | 10.4 | 10.4
M4X8 Buttonhead Screw (pack of 100) | https://www.mcmaster.com/products/screws/rounded-head-screws~/metric-18-8-stainless-steel-button-head-hex-drive-screws/thread-size~m4/length~8-mm/finish~passi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 | 1 | 10.09 | 10.09
Total: |  |  |  | 1223.44
Bowden Tube | https://www.amazon.com/Jagwire-Sport-Housing-Slick-Lube-Titanium/dp/B085NBZMJS?s=sporting-goods | 1 | 61.97

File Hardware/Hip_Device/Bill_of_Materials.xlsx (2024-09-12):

Part | Quantity | Price (9/18/23) | Total Price | Notes | Link
Motor
AK60v1.1 Motor | 2 | 298.90 | 597.80 |  | https://store.tmotor.com/goods-1201-AK60-6+V11.html
External Manufactured Parts
Abduciton/Adduction Block - Hip | 2 | 103.50 | 207.00 | Refer to documentation for ordering information and files | https://uptivemfg.com/
Abduciton/Adduction Block - Leg | 2 | 103.50 | 207.00 | Refer to documentation for ordering information and files | https://uptivemfg.com/
Printed Circuit Board | 1 | 59.92 | 0.00 | Refer to documentation for ordering information and necessary files; Initial order was for 5 boards so price is estimated as 1/5th that price | https://jlcpcb.com/
Carbon Fiber Parts - Internally Manufactured
Carbon Fiber - Upright | 1 | 173.99 | 173.99 | Recommended stock should have enough for multiple uprights of varying lengths (e.g., short and long versions of uprights) | https://www.rockwestcomposites.com/25502-group
Carbon Fiber Plate | 1 | 60.25 | 60.25 | Part Number: 8181K14; For: Motor Adaptors (Inner and Outer), Spacer, and Motor-to-Upright; Totals 8 Parts | https://www.mcmaster.com/8181K14/
3D Printed Parts - Internally Printed
Upright Bolt Support | 2 | 2.44 | 4.88 | Printed with Onyx using a Markforged Mark Two; Price is estimated based on material used from printer; See Solidworks files located within documentation | N/A
HoleTemplateForUpright | 1 | 1.60 | 1.60
Motor-to-Leg Shell | 2 | 1.81 | 3.62
Thigh Cuffs - Right | 1 | 77.80 | 77.80
Thigh Cuffs - Left | 1 | 80.61 | 80.61
Thigh Cuffs - Back | 2 | 8.91 | 17.82
Thigh Cuffs - Top Slider | 2 | 9.13 | 18.26
Thigh Cuffs - Bottom Slider | 2 | 9.47 | 18.94
FSR Puck Plate | 4 | 1.05 | 4.20
Backplate | 1 | 24.37 | 24.37
Battery Cover | 1 | 11.86 | 11.86
Electrical Box Cover - Shell | 1 | 22.32 | 22.32
Electrical Box Cover - Internal | 1 | 4.55 | 4.55
Strain Relief for PCB Wires (left) | 1 | 1.31 | 1.31
Strain Relief for PCB Wires (right) | 1 | 1.28 | 1.28
PCB Spacer | 1 | 1.05 | 1.05
Hardware - Mounting Plates to Belt
PVC/Acrylic Plate Mounting Plates | 2 | 18.77 | 37.54 | Part Number: 8650K21, Grey | https://www.mcmaster.com/8650K21-8650K214/
Aluminum Hex Nut - M5 x 0.8 mm | 16 | 0.13 | 2.07 | Part Number: 91854A102; Only comes in pack of 50, price is estimated on a per part basis | https://www.mcmaster.com/91854a102/
Button Head Hex Drive Screw - M5 x 0.8 mm; Length: 22 mm | 8 | 0.26 | 2.10 | Part Number: 91239A242, Only comes in pack of 50, price is estimated on a per part basis | https://www.mcmaster.com/91239A242/
Aluminum Washer - M5 Screw Size | 8 | 1.08 | 8.66 | Part Number: 92334A113; Only comes in pack of 10, price is estimated on a per part basis | https://www.mcmaster.com/92334A113/
Nylon 6/6 Plastic Cap Nut | 8 | 0.26 | 2.08 | Part Number: 90527A510; Only Comes in Pack of 100, price is estimated on a per part basis | https://www.mcmaster.com/90527A510/
Hardware - Electrical Box
Zinc-Plated Steel Button Head Torx - M3 x 0.5 mm; Length 14 mm | 4 | 0.19 | 0.74 | Part Number: 92832A566; Only comes in pack of 50, price estimated on a per part basis | https://www.mcmaster.com/92832A566/
Aluminum Waher - M3 Screw Size | 4 | 1.04 | 4.16 | Part Number: 92334A109, Only comes in pack of 10, price estimated on per part basis | https://www.mcmaster.com/92334A109/
Medium-Strength Steel Thin Hex Nut - M3 x 0.5 mm | 2 | 0.06 | 0.11 | Part Number: 90370A203, Only comes in pack of 100, price estimated on a per part basis | https://www.mcmaster.com/90370A203/
Alloy Steel Socket Head Screw - M3 x 0.5 mm; Length 10 mm | 7 | 0.10 | 0.67 | Part Number: 91290A115, Only comes in pack of 100, price estimated on a per part basis | https://www.mcmaster.com/91290A115/
Heat-Set Inserts for Plastic - M3 x 0.5 mm | 15 | 0.28 | 4.27 | Part Number: 94459A130, Only comes in pack of 50, price estimated on a per part basis | https://www.mcmaster.com/94459A130/
M2.5 x 0.5 Tap | 1 | 11.99 | 11.99 | Might be able to get away with not using this | https://www.amazon.com/Aceteel-Metric-Thread-Machine-M2-5x0-5mm/dp/B09SHPBP22
Button Head Hex Drive Screw - M2.5 x 10 mm | 2 | 0.39 | 0.77 | Part Number: 91239A757, Only comes in pack of 25, price estimated on a per part basis | https://www.mcmaster.com/91239A757/
Hardware - Motor to Belt
Stainless Steel Ball Bearing - 6mm Shaft Diameter | 4 | 8.74 | 34.96 | Part Number: 7804K143 | https://www.mcmaster.com/7804K143/
Metal Sealing Washer - M6 Screw Size | 4 | 0.35 | 1.41 | Part Number: 97725A102, Only comes in pack of 50, price is estimated on a per part basis | https://www.mcmaster.com/97725A102/
Stainless Steel Low-Profile Precision Shoulder Screw - 6 mm Diameter; Length: 25 mm | 2 | 10.89 | 21.78 | Part Number: 90323A466 | https://www.mcmaster.com/90323A466/
Stainless Steel M5 Locknut | 2 | 0.15 | 0.29 |  | https://www.mcmaster.com/94205A240/
Button Head Hex Drive Screw - M5 x 0.8 mm; Length: 14 mm | 8 | 0.16 | 1.28 | Part Number: 91239A230; Only comes in pack of 100, price is estimated on a per part basis | https://www.mcmaster.com/91239A230/
Aluminum Hex Nut - M5 x 0.8 mm | 8 | 0.26 | 2.07 | Part Number: 91854A102; Only comes in pack of 50, price is estimated on a per part basis | https://www.mcmaster.com/91854A102/
Zinc-Plated Alloy Steel Button Head Torx Screws - M3 x 0.5 mm; Length: 6 mm | 8 | 0.08 | 0.65 | Part Number: 92832A215, Only comes in pack of 100, price is estimated on a per part basis | https://www.mcmaster.com/92832A215/
Alloy Steel Socket Head Screw - M3 x 0.5 mm; Length: 4 mm | 18 | 0.13 | 2.33 | Part Number: 91290A109; Only comes in pack of 100, price is estimated on a per part basis | https://www.mcmaster.com/91290A109/
Hardware - Upright to Motor
Alloy Steel Socket Head Screw - M3 x 0.5 mm; Length: 10 mm | 12 | 0.10 | 1.14 | Part Number: 91290A115; Only comes in pack of 100; price is estimated on a per part basis | https://www.mcmaster.com/91290A115/
Button Head Torx Screw - M5 x 0.8 mm; Length 30 mm | 6 | 0.37 | 2.20 | Part Number: 90910A582; Only comes in pack of 25, price is estimated on a per part basis | https://www.mcmaster.com/90910A582/
Aluminum Washer - M5 Screw Size | 6 | 1.09 | 6.55 | Part Number: 92334A113, Only comes in pack of 10, price is estimated on a per part basis | https://www.mcmaster.com/92334A113/
Aluminum Hex Nut - M5 x 0.8 mm | 6 | 0.26 | 1.56 | Part Number: 91854A102; Only comes in pack of 50, price is estimated on a per part basis | https://www.mcmaster.com/91854A102/
Electrical - CAN Wire
Motor-to-Board CAN Wire - CABLE 2COND 28AWG CLEAR SHLD 25' | 2 | 5.98 | 11.96 | Digi-Key Part Number: CI28E-25-ND; Part comes in 25 feet, price estimated based on length used (~19 inches) | https://www.digikey.com/en/products/detail/969M101-28-1TPS-025/CI28E-25-ND/3526257?itemSeq=386416477
CJT Connectors - Motor End | 2 | 0.03 | 0.07 | LCSC Part Number: C339040; Only comes in pack of 20, price estimated on a per part basis | https://www.lcsc.com/product-detail/Rectangular-Connectors-Housings_CJT-Changjiang-Connectors-A1257H-4P_C339040.html
CJT Pins - Motor End | 4 | 0.01 | 0.04 | LCSC Part Number: C339052; Only comes in pack of 100, price estimated on a per part basis | https://www.lcsc.com/product-detail/Line-Pressing-Terminals_CJT-Changjiang-Connectors-A1257-TP_C339052.html
Molex Pins - Board End | 4 | 0.12 | 0.48 | Digi-Key Part Number: WM7933-ND | https://www.digikey.com/en/products/detail/molex/5013340100/1531513
Molex Connectors- Board End | 2 | 0.32 | 0.64 | Digi-Key Part Number: WM7915-ND | https://www.digikey.com/en/products/detail/molex/5013300200/1531499
Electrical - FSRs
Force Sensitve Resistors (FSRs) | 4 | 27.82 | 111.27 | Comes in pack 4 | https://www.tekscan.com/products-solutions/force-sensors/flexiforce-a502-sensor
Wire - FSRs (Ribbon Cable) | 8 | 0.33 | 2.66 | Has ten pins, only need two for each FSR; price estimated on a per foot basis | https://www.amazon.com/risingsaplings-Ribbon-Rainbow-1-27mm-2-54mm/dp/B097C84H9W
FSR - Male and Female Pin Headers | 8 | 0.45 | 3.60 | Contains 20 of each, only need 8; price estimated on per pair basis | https://www.amazon.com/2-54mm-Breakaway-Female-Connector-Arduino/dp/B01MQ48T2V
Electrical - FSR to Board Wire
FSR-to-Board Connecting Cable - CABLE 4COND 28AWG BLACK SHLD 5M | 1 | 21.97 | 21.97 | Digi-Key Part Number:T1319-5-ND; Part comes in 5 meters, price estimated based on length used (~ 4ft) | https://www.digikey.com/en/products/detail/tensility-international-corp/30-00491/5819490
Ribbon Cable Header for Board- CONN RCPT 8POS IDC 28AWG GOLD | 2 | 2.11 | 4.22 |  | https://www.digikey.com/en/products/detail/w%C3%BCrth-elektronik/61200823021/4846918
Ribbon Cable | 2 | 0.33 | 0.67 | Has 10 pins but only need eight, can use other two for FSRs; Price based on a per foot basis | https://www.amazon.com/risingsaplings-Ribbon-Rainbow-1-27mm-2-54mm/dp/B097C84H9W
Electrical - Power Switch
Xt30 Male and Female - For Battery-to-Board Connection & Motor to Board | 1 | 0.86 | 0.86 | Comes in a pack of 10 (also include XT30 Female and Heat Shrink, so you could use to make own power cables); price esimtated on per part basis | https://www.amazon.com/10Pairs-Upgrade-Connector-Female-Battery/dp/B08P5HVMYT
Xt60 Male - For Battery-to-Board Connection | 1 | 1.00 | 1.00 | Comes in pack of 10, price estimated on a per part basis | https://www.amazon.com/XT60E-M-Mountable-Connector-Models-Multicopter/dp/B07YJMCDC3?th=1
Switch | 1 | 2.13 | 2.13 | Digi-Key Part Number: EG1529-ND | https://www.digikey.com/en/products/detail/e-switch/R5ABLKBLKFF0/301976
25 FT 16 AWG Electrical Wire | 1 | 11.98 | 11.98 |  | https://www.amazon.com/Electrical-Conductor-parallel-silicone-Extension/dp/B07RRPFL3Q
16 AWG Quick Disconnect Terminals | 2 | 0.10 | 0.20 |  | https://www.amazon.com/TICONN-Disconnect-Connectors-Electrical-Assortment/dp/B08BZ972B5?cv_ct_cx=ticonn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
Electrical - Motor Power Cables
16 AWG Wire | Price Factored Above |  |  | Comes in a pack of 10 (also include XT30 Female and Heat Shrink, so you could use to make own power cables); price esimtated on per part basis | https://www.amazon.com/Electrical-Conductor-parallel-silicone-Extension/dp/B07RRPFL3Q
Xt30 Male and Female - For Battery-to-Board Connection & Motor to Board | Price Factored Above |  |  | Comes in a pack of 10 (also include XT30 Female and Heat Shrink, so you could use to make own power cables); price esimtated on per part basis | https://www.amazon.com/10Pairs-Upgrade-Connector-Female-Battery/dp/B08P5HVMYT
Heat Shrink | Price Factored Below |  |  | Digi-Key Part Number: EG1529-ND | https://www.amazon.com/650pcs-Shrink-Tubing-innhom-Approved/dp/B07WWWPR2X?hvadid=664381657194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
Electrical - Other
Battery | 1 | 37.99 | 37.99 | Comes in pack of 2, price estimated on a per part basis | https://www.amazon.com/HRB-1800mAh-Helicopter-Airplane-Multicopter/dp/B088QXJNJV/
TICOON Nylon Spade Female Terminals | 2 | 0.09 | 0.18 | Contains pack of 100, price estimated on a per part basis | https://www.amazon.com/TICONN-Disconnect-Connectors-Electrical-Assortment/dp/B08BZ972B5?cv_ct_cx=ticonn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
Arduino Nano 33 BLE (with Headers) | 1 | 31.25 | 31.25 | Digi-Key Part Number: 1050-ABX00034-ND | https://www.digikey.com/en/products/detail/arduino/ABX00034/10239973
Teensy 4.1 (with Headers) | 1 | 37.28 | 37.28 | Digi-Key Part Number: 1568-DEV-16996-ND | https://www.digikey.com/en/products/detail/sparkfun-electronics/DEV-16996/13158152
RGB LED | 1 | 2.04 | 2.04 | Digi-Key Part Number: 754-2153-ND | https://www.digikey.com/en/products/detail/kingbright/WP154A4SEJ3VBDZGC-CA/7597097
Heat Shrink - FSRs and Cables (CAN, FSR-to-Board, Battery Connectors) | 1 | 9.96 | 9.96 | Just listed as one part price wise but contains all you need for device and much more | https://www.amazon.com/650pcs-Shrink-Tubing-innhom-Approved/dp/B07WWWPR2X?hvadid=664381657194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
Thigh Cuffs
Denser Hook & Loop Adehsive Tape | 1 | 10.99 | 10.99 | You don't need full amount, Price listed as full amount due to challenge of estimate amount used | https://www.amazon.com/Denser-Sticky-Adhesive-Fastener-Strips/dp/B07N3B36Z2?th=1
3 mm thick Velcro Brand Fastener Compatible UBL Neoprene | 1 | 65.00 | 65.00 | 3mm Thick; Color: Black; You don't need full amount, Price listed as full amount due to challenge of estimating amount used | https://www.seattlefabrics.com/Velcroreg-Brand-Fastener-Compatible-UBL-Neoprene-by-the-Linear-Foot-starting-4500-per-linear-foot_p_843.html
Velcro Fastener | 1 | 1.36 | 1.36 | Comes in a pack of 5, you only need 2-4, price estimated on a per part basis | https://www.securecableties.com/18-x-2-inch-cinch-straps-5-pack
Aluminum Hex Nut - M5 x 0.8 mm | 4 | 0.26 | 1.04 | Part Number: 91854A102; Only comes in pack of 50, price is estimated on a per part basis | https://www.mcmaster.com/91854A102/
Screw - M5 x Length: 12 | 4 | 0.12 | 0.49 | Part Number: 91306A666; Only comes in pack of 100, price is estimated on a per part basis | https://www.mcmaster.com/91306A666/
Aluminum Washer - M5 Screw Size | 4 | 1.08 | 4.33 | Part Number: 92334A113, Only comes in pack of 10, price is estimated on a per part basis | https://www.mcmaster.com/92334A113/
Cam Handle - M3 x 0.5 mm; Length: 15 mm | 2 | 15.02 | 30.04 | Part Number: 5720K241 | https://www.mcmaster.com/5720K241/
Button Head Hex Drive Screw - M3 x 0.5 mm; Length: 16 mm | 2 | 0.09 | 0.19 | Part Number: 92095A184; Only comes in pack of 100, price is estimated on a per part basis | https://www.mcmaster.com/92095A184/
M3 Nut | 4 | 0.06 | 0.23 | Part Number: 90370A203, Only comes in pack of 100, price estimated on a per part basis | https://www.mcmaster.com/90370A203/
Misc
Hip Belt | 1 | 39.00 | 39.00 | Any similar waist belt will suffice, this product may have limited quantities, we will update this information and guide if we switch to new one | https://www.moosejaw.com/p/osprey-womens-isoform-cm-hipbelt-23trywsfrmcmhpbltbag/23trywsfrmcmhpbltbag?sku=25482757&gad_source=1&gclsrc=aw.ds
SD Card | 1 | 10.96 | 10.96 | 32 GB is enough | https://www.amazon.com/SanDisk-Extreme-microSDHC-UHS-3-SDSQXAF-032G-GN6MA/dp/B06XWMQ81P?rnid=2528832011&s=electronics
EVA Foam (White) [Optional] | 1 | 17.19 | 17.19 | 500 mm x 1500 mm, 6 mm Thick; Used for Insoles and Hip Belt Padding | https://thecosplaypros.com/products/eva-foam-sheets?variant=31293426860167
ESTIMATED PRICE | $2165.14 |  |  |  | This price is an estimate, does not include the cost of shipping associated with purchased parts and manufacuring of some components nor the tools needed to manufacture some of the components

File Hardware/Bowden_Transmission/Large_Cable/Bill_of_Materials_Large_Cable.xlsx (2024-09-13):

Item | Link | Count | Price ($) | Total ($)
Machined Parts
Sprocket (x2) AND Cable - Chain Interface (x4) | https://www.hubs.com/ | 1 | 562.24 | 562.24
Prefabricated Parts
Chain Master Link | https://www.mcmaster.com/catalog/130/1314/6027K71 | 4 | 1.83 | 7.32
05B Chain (2ft) | https://www.mcmaster.com/catalog/130/1314/6027K71 | 1 | 18 | 18
TMotors AK80-9 | https://www.cubemars.com/goods-982-AK80-9.html | 2 | 570.9 | 1141.8
6mm x 13mm x 5mm Flanged Ball Bearing (package of 10) | https://www.amazon.com/HiPicco-Flanged-Bearing-Shielded-Bearings/dp/B0CRLFPJPG?th=1 | 1 | 7.99 | 7.99
Large Steel Cable (250 ft) | https://www.amazon.com/Stainless-Steel-Aircraft-Cable-T304/dp/B00THGVV9W | 1 | 37.5 | 37.5
Large Cable Crimps (pack of 50) | https://www.mcmaster.com/3926T32/ | 1 | 11.54 | 11.54
Fasteners
M3X8 Buttonhead Screw (pack of 100) | https://www.mcmaster.com/products/screws/system-of-measurement~metric/rounded-head-screws~/metric-18-8-stainless-steel-button-head-hex-drive-screws/thread-siz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 | 1 | 8 | 8
M3X6 Buttonhead Screw (pack of 100) | https://www.mcmaster.com/products/screws/system-of-measurement~metric/rounded-head-screws~/metric-18-8-stainless-steel-button-head-hex-drive-screws/finish~pas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 | 1 | 5.83 | 5.83
M3X30 Flathead Screw (pack of 50) | https://www.mcmaster.com/products/screws/flat-head-screws~/metric-alloy-steel-hex-drive-flat-head-screws/thread-size~m3/length~30-mm/ | 1 | 6.93 | 6.93
M5X20 Buttonhead Screw (pack of 50) | https://www.mcmaster.com/products/screws/rounded-head-screws~/metric-18-8-stainless-steel-button-head-hex-drive-screws/thread-size~m5/length~20-mm/finish~pass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 | 1 | 12.38 | 12.38
M5 Lock Nuts (pack of 50) | https://www.mcmaster.com/products/nuts/locknuts~/nylon-insert-locknuts~~/system-of-measurement~metric/thread-size~m5/material~stainless-steel-2/ | 1 | 7.26 | 7.26
M3 Washer (pack of 10) | https://www.mcmaster.com/products/washers/washers-2~/metric-general-purpose-washers/screw-size~m3/material~aluminum-1/ | 1 | 10.4 | 10.4
M4X8 Buttonhead Screw (pack of 100) | https://www.mcmaster.com/products/screws/rounded-head-screws~/metric-18-8-stainless-steel-button-head-hex-drive-screws/thread-size~m4/length~8-mm/finish~passi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 | 1 | 10.09 | 10.09
Total: |  |  |  | 1847.28
Bowden Tube | https://catalog.lexcocable.com/item/conduit--casing-housing-/flat-stock-coiled-steel-bicycle-type-conduit/-7mm2p | 1

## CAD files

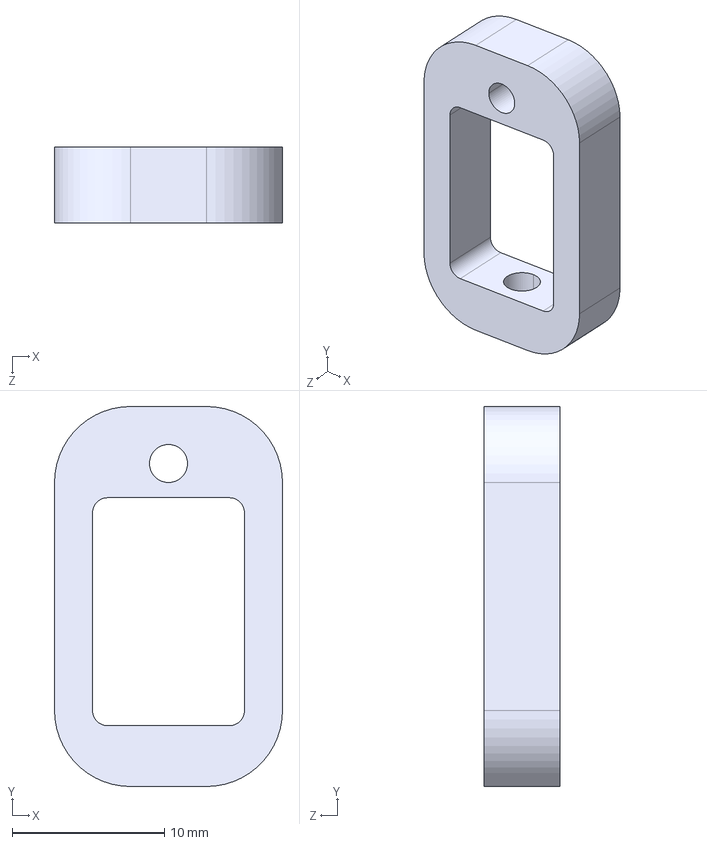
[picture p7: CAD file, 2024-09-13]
Hardware/Bowden_Transmission/Large_Cable/Universal Cable Chain Interface/UCCI.STEP
15.0 x 25.0 x 5.00 mm

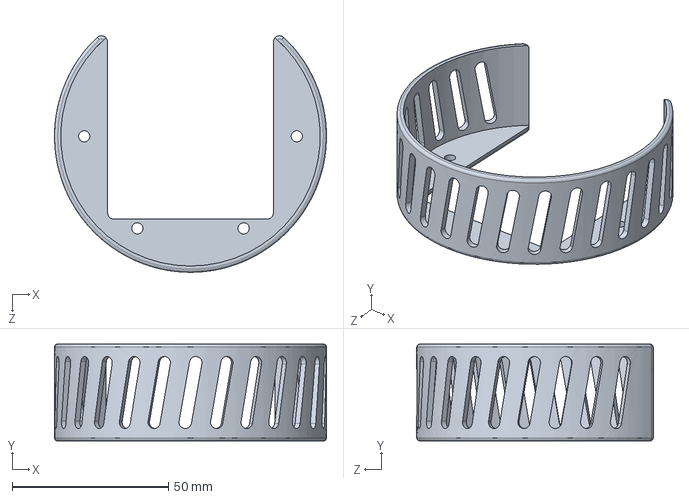
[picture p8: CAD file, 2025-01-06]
Hardware/Bowden_Transmission/Parts/AK60V1.1/3D_Printed_Parts/Heat_Shield (Optional)/ak60v1_1HeatShield.SLDPRT
87.0 x 31.0 x 75.7 mm

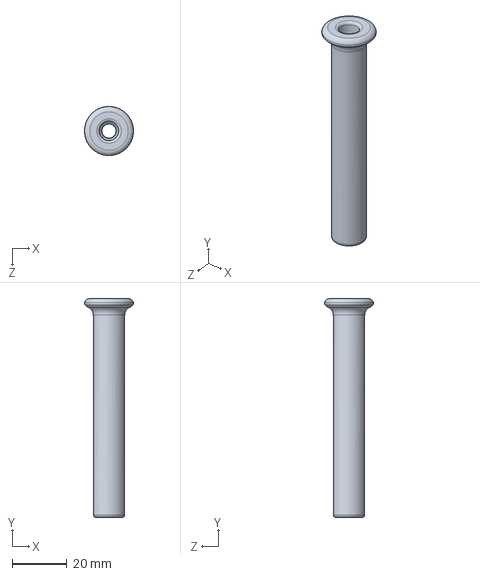
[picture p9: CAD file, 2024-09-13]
Hardware/Bowden_Transmission/Parts/AK60V1.1/3D_Printed_Parts/Strain_Relief_Inserts_TPU.SLDPRT
17.9 x 80.0 x 17.9 mm

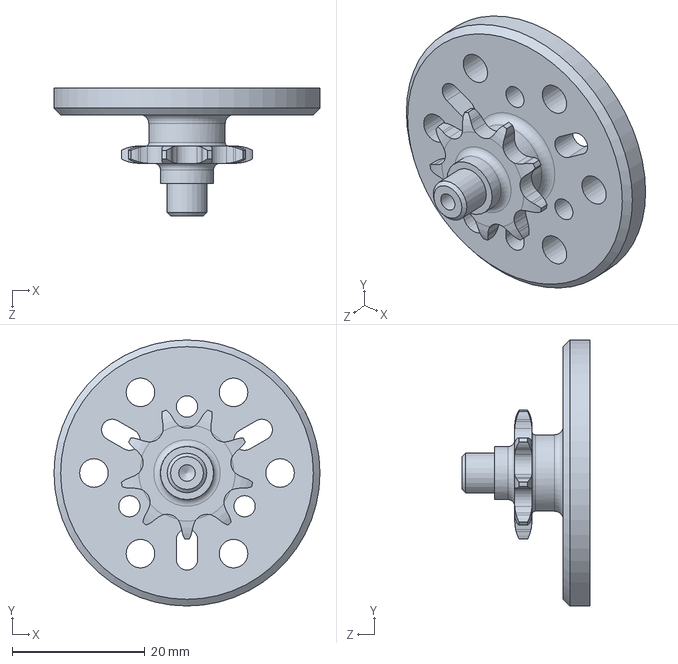
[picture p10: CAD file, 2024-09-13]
Hardware/Bowden_Transmission/Parts/AK60V1.1/Machined_Parts/Sprocket_AK60V1_1.SLDPRT
40.0 x 40.0 x 19.2 mm

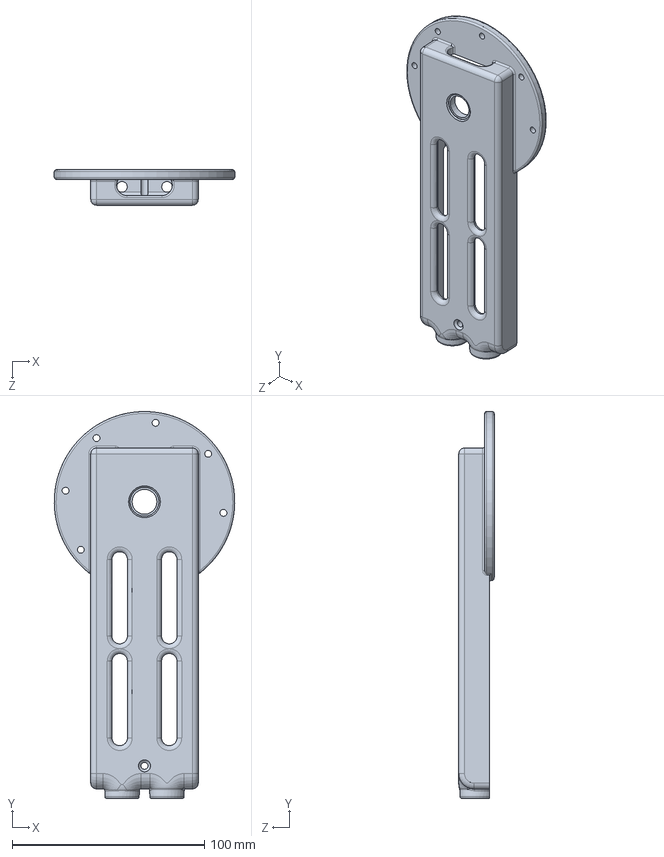
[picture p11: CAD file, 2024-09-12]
Hardware/Bowden_Transmission/Parts/AK70/3D_Printed_Parts/Cartridge_AK70.SLDPRT
94.0 x 201.5 x 18.5 mm

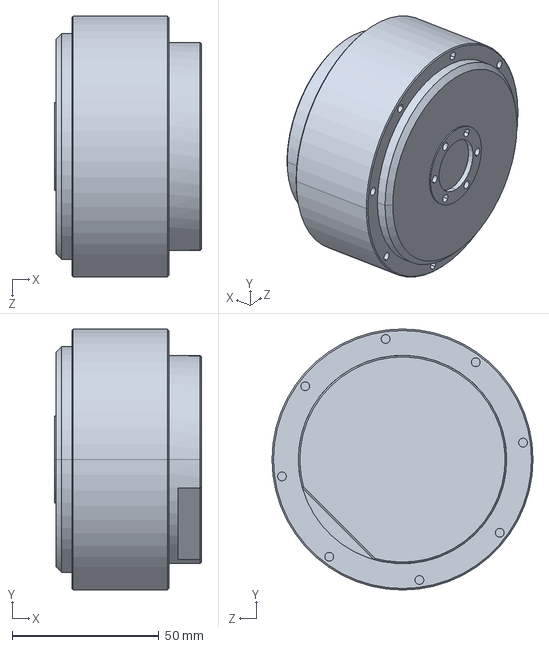
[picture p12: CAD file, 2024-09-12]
Hardware/Bowden_Transmission/Parts/AK70/AK70-10.SLDPRT
50.2 x 89.0 x 89.0 mm

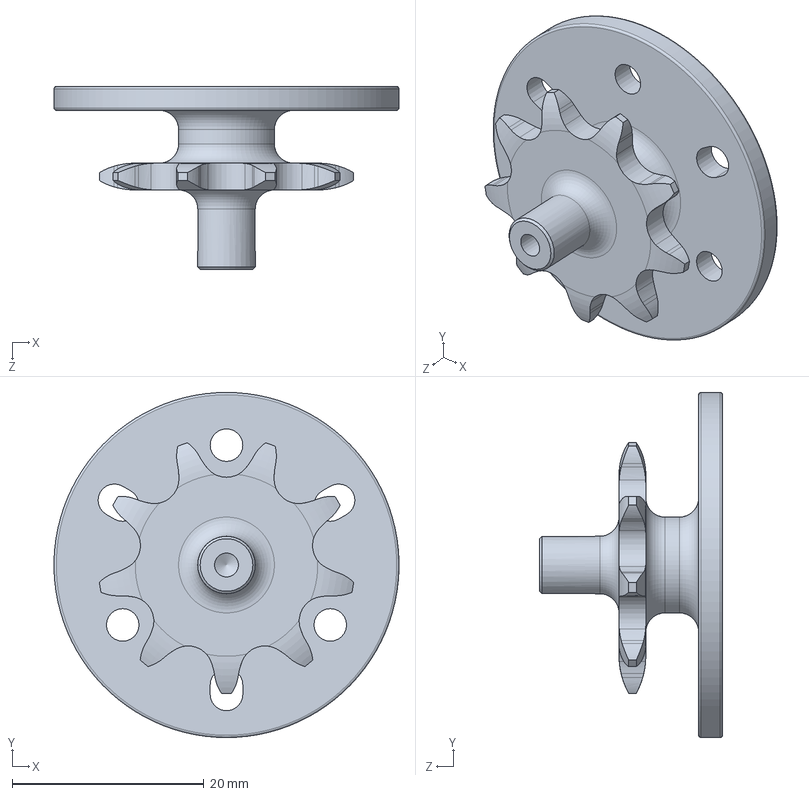
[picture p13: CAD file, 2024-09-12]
Hardware/Bowden_Transmission/Parts/AK70/Machined_Parts/Sprocket_AK70.SLDPRT
36.0 x 36.0 x 19.1 mm

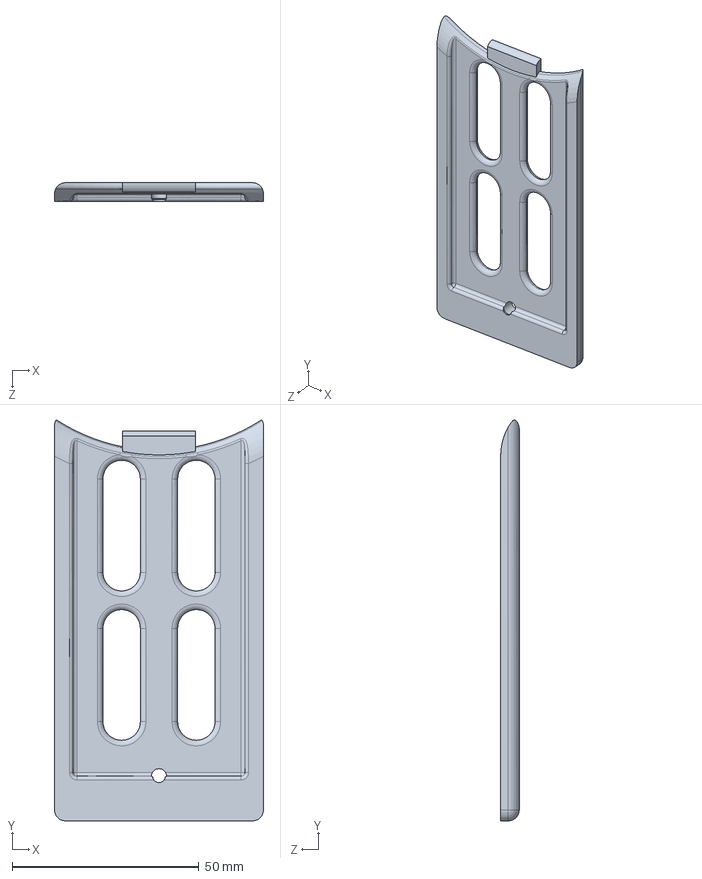
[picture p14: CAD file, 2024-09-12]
Hardware/Bowden_Transmission/Parts/AK80/3D_Printed_Parts/Back_Cover_AK80.SLDPRT
56.0 x 107.4 x 5.00 mm

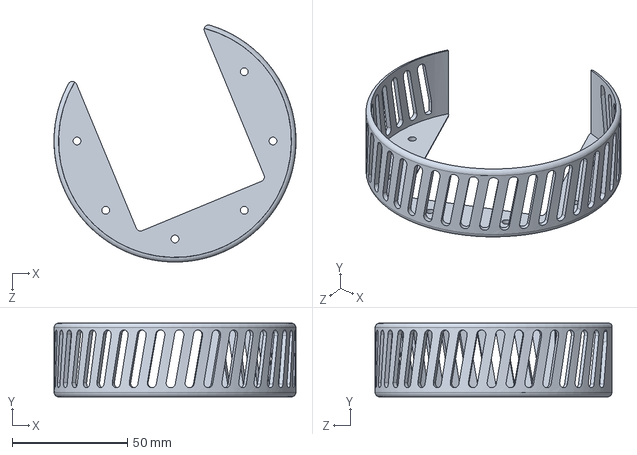
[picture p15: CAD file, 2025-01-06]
Hardware/Bowden_Transmission/Parts/AK80/3D_Printed_Parts/Heat_Shield (Optional)/ak80HeatShield.SLDPRT
105.0 x 32.0 x 102.8 mm

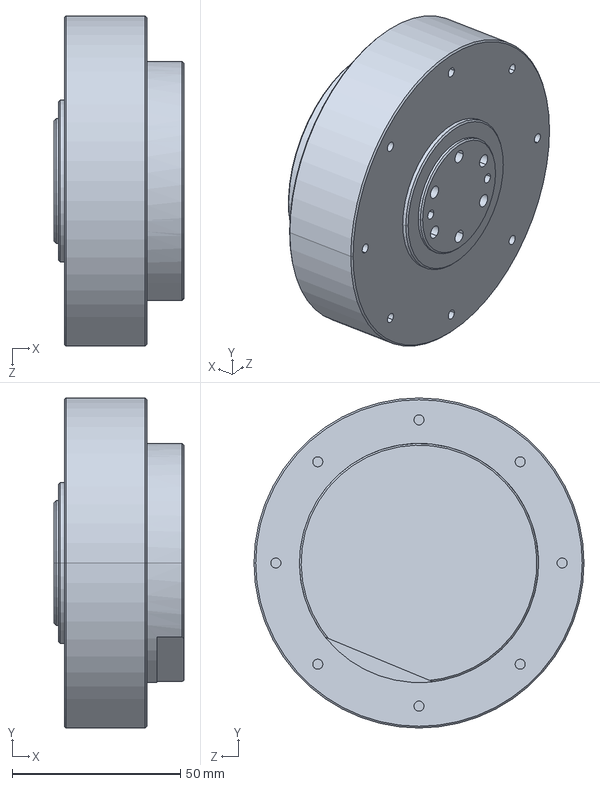
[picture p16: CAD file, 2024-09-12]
Hardware/Bowden_Transmission/Parts/AK80/AK80-9.SLDPRT
38.5 x 98.0 x 98.0 mm

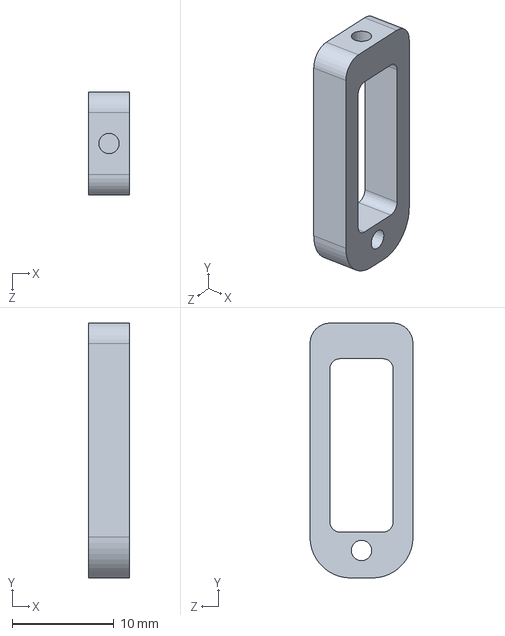
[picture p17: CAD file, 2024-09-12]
Hardware/Bowden_Transmission/Parts/AK80/Machined_Parts/Cable_Chain_Interface.SLDPRT
4.00 x 25.0 x 10.1 mm

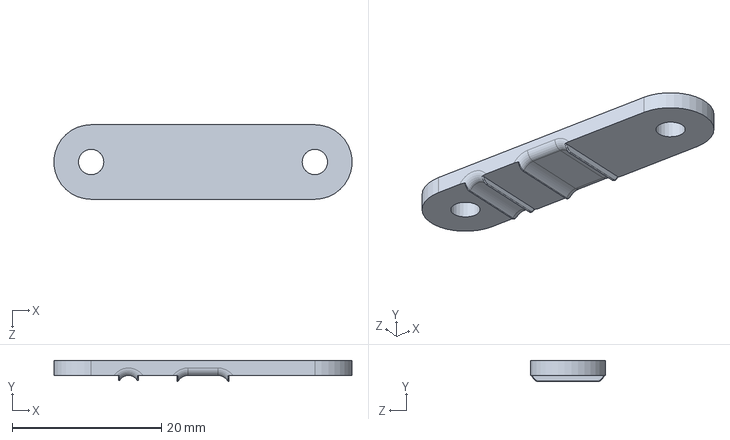
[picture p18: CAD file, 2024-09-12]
Hardware/Bowden_Transmission/Parts/MotorCableStrainRelief.SLDPRT
40.0 x 2.82 x 10.0 mm

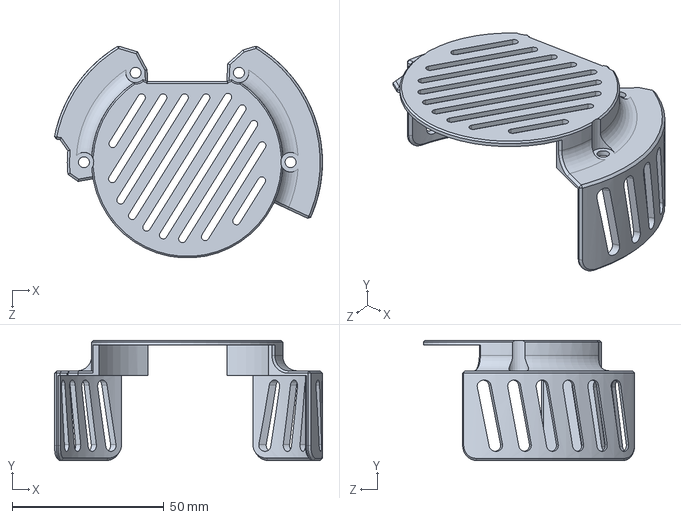
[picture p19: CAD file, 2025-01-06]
Hardware/Hip_Device/Part Files for 3D Printing/Heat_Shield (Optional)/hipHeatShield.SLDPRT
88.2 x 39.5 x 69.6 mm

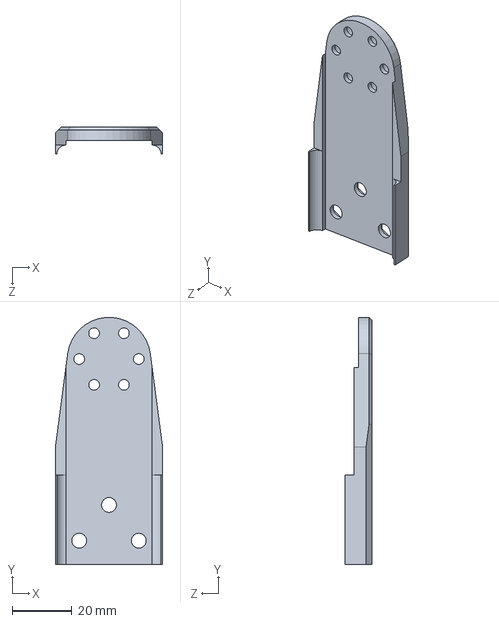
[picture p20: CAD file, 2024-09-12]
Hardware/Hip_Device/Part Files for 3D Printing/motorToStrut.SLDPRT
36.0 x 82.9 x 9.09 mm

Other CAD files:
Hardware/Hip_Device/Part Files for Machining/Aluminum Machining/adAbductionBlockHipSide.SLDPRT
Hardware/Hip_Device/Part Files for Machining/CF Machining/hipAdapterOuter.SLDPRT
Hardware/Bowden_Transmission/Parts/AK60V1.1/3D_Printed_Parts/Back_Cover_AK60V1_1(1).SLDPRT
Hardware/Bowden_Transmission/Parts/AK60V1.1/Machined_Parts/Cable_Chain_Interface_AK60V1.1.SLDPRT
Hardware/Bowden_Transmission/Large_Cable/Universal Cable Chain Interface/UCCI.SLDDRW
Hardware/Bowden_Transmission/Large_Cable/Universal Cable Chain Interface/UCCI.SLDPRT
Hardware/Bowden_Transmission/Large_Cable/Universal Cable Chain Interface/UCCI.STL
Hardware/Bowden_Transmission/Parts/AK60V1.1/3D_Printed_Parts/Back_Cover_AK60V1_1.SLDPRT
Hardware/Bowden_Transmission/Parts/AK60V1.1/3D_Printed_Parts/Belt_to_Motor_AK60V1_1.SLDPRT
Hardware/Bowden_Transmission/Parts/AK60V1.1/3D_Printed_Parts/Cartridge_AK60V1_1.SLDPRT
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

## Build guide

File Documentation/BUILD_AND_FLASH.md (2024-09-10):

## Downloads
1. Download Arduino IDE 1.8.19, which can be found [here](https://www.arduino.cc/en/software) or [here](https://drive.google.com/drive/folders/1IRxJFNm2gxUtCeU8Dcavg_Mv2ubANOHK?usp=drive_link)
2. Now install Teensyduino, which can be found [here](https://www.pjrc.com/teensy/td_download.html) or [here](https://drive.google.com/drive/folders/1IRxJFNm2gxUtCeU8Dcavg_Mv2ubANOHK?usp=drive_link). Be sure to install the 1.56 version for your system.
3. Install the Arduino Nano 33 BLE through the Arduino Boards Manager.  
3. Install the Arduino libraries according to [Libraries](#libraries).

## Flashing
Now that you have all of the tools installed, lets flash.
1. Connect your computer to the Teensy using a micro-USB cable. 
2. Change the Board to the Teensy 4.1
3. Change the Arduino port to use the Teensyduino port. The correct port will have the board name to the right of the COM (Windows Only) port.
4. Make sure that the Board Version is properly set in the Config.h
5. Press the Arrow button on the Arduino IDE to upload the code to the Teensy. 
6. Change the Board to the Arduino Nano 33 BLE.
7. Change the Arduino port in the same manner as step 3. 
8. Press the upload button. Note: The Nano will take much longer to build than the Teensy. 

## Libraries
All of the files in the libraries directory of this codebase should be copied to
C:\Users\\\[USER\]\Documents\Arduino\libraries\ or system equivalent. This will
'install' the libraries on your system. 
Details on the libraries can be found in the [Libraries Folder](/Libraries).

## Arduino Boards Manager
To open the boards manager press:
Tools -> Board -> Boards Manager

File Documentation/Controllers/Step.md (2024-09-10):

# Step Controller

## Description
This controller attempts to apply a constant torque at the joint for a set duration and for a set number of times.

## Parameters
Parameter index order can be found in [ControllerData.h](/ExoCode/src/ControllerData.h).
- amplitude - Magnitude of the applied torque, in Nm
- duration - Duration of the applied torque
- repetitions - Number of times the torque is applied
- spacing - Time between each application of torque 
- use_pid - This flag turns PID on(1) or off(0)
- p_gain - Proportional gain for closed loop controls
- i_gain - Integral gain for closed loop controls
- d_gain - Derivative gain for closed loop controls
- alpha - Filtering term for exponentially wieghted moving average (EWMA) filter, used on torque sensor to cut down on noise.

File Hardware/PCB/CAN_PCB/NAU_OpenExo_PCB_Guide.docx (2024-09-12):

# Introduction

This guide details the main components of the printed circuit board (PCB) for the NAU OpenExo and provides instructions on how to order the PCB and its assembly from a manufacturer. Resources on PCB background and design can be found on websites such as Sparkfun (https://learn.sparkfun.com/tutorials/pcb-basics/all), KiCad (https://www.kicad.org/), and EasyEDA (https://easyeda.com/),

# PCB Background

This custom-designed PCB is a crucial part of the NAU OpenExo (exo) system. It communicates with the external control application, receives commands, and performs motor control based on predefined algorithms.

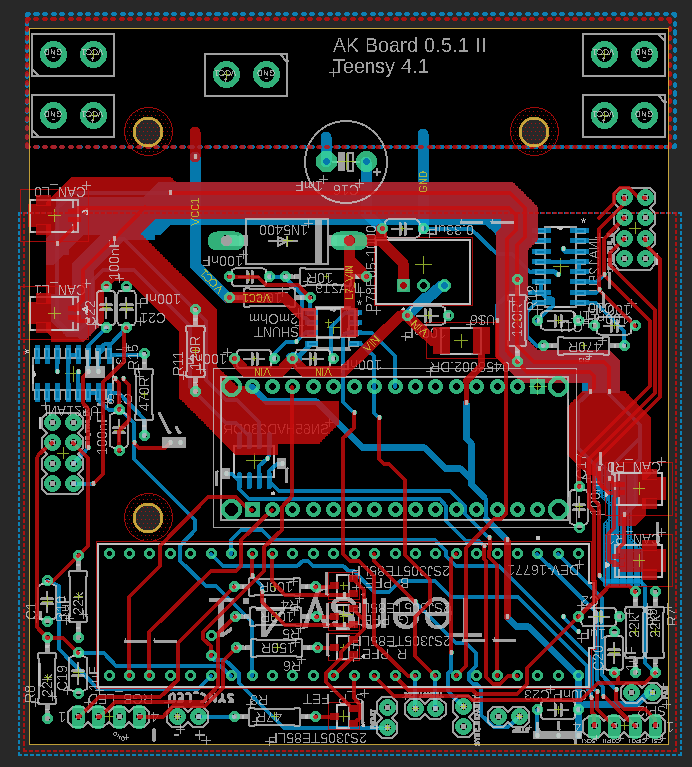
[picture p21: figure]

Figure 1: PCB - Top Layer (Red), Bottom Layer (Blue)

Key Components

- DC-DC converter (P78E05-1000): This component converts the battery voltage to 5V DC in order to properly power onboard components such as the Arduino Nano and Teensy 4.1.

Important Note: Capacitor C16 may need to be replaced if a battery with higher voltage output is used (Example Replacement: MAL217250471E3).

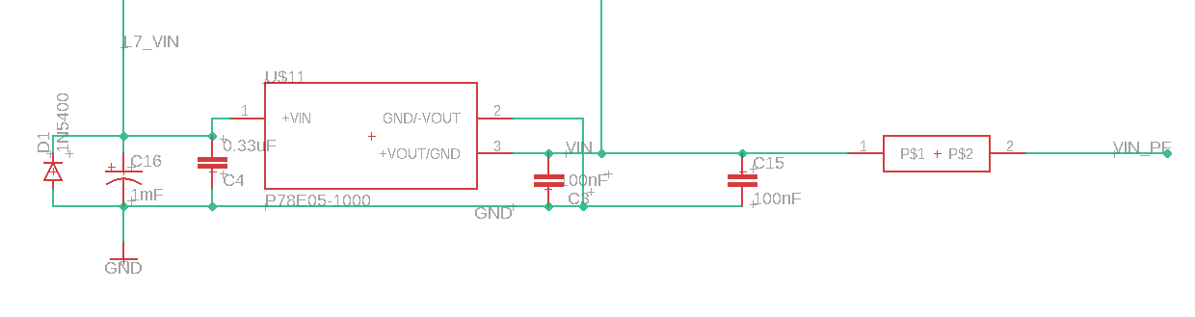
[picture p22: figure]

- Development boards (Arduino Nano 33 BLE and Teensy 4.1): These boards provide the main computing power for the PCB. The Arduino Nano handles communication between the exo and the external control application, while the Teensy 4.1 processes sensor data and controls the motors based on the high-level controller. All variations of Teensy 4.1 are compatible, but some libraries may need to be added depending on the version.

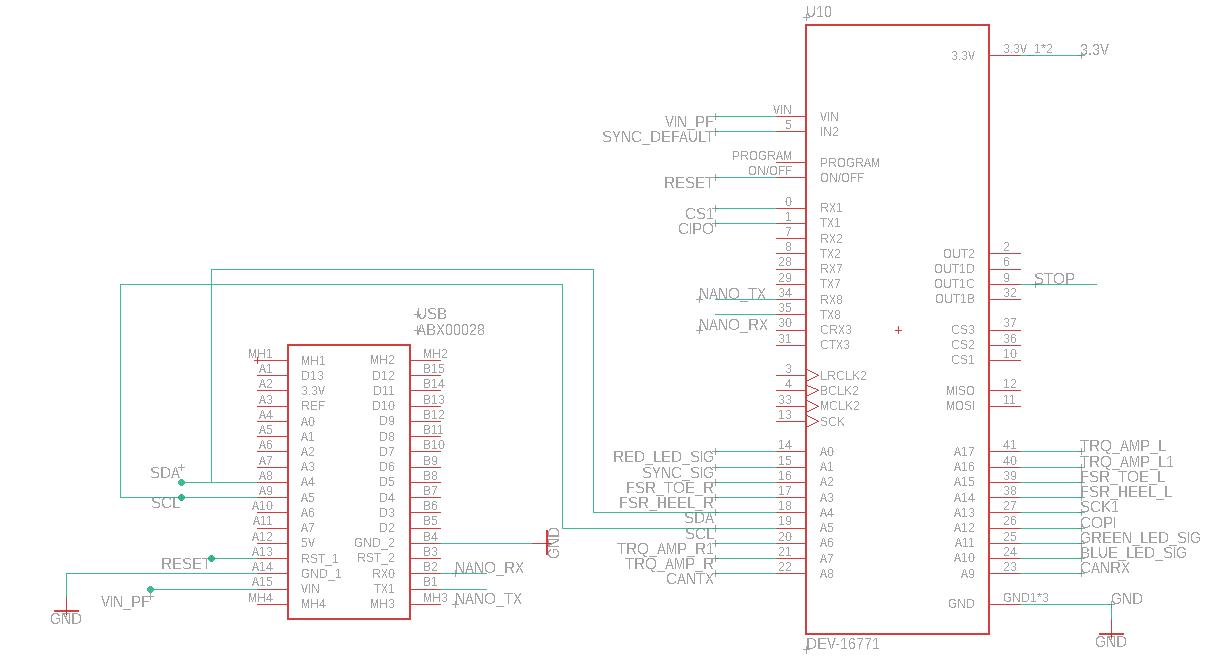
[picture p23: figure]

- CAN interface (SN65HVD230DR): This interface serves as the communication link between the CAN transceiver pins and the receiver pins on the Teensy 4.1, as well as the motors. A keep out area is created around the CAN interface traces to reduce the electromagnetic interference.

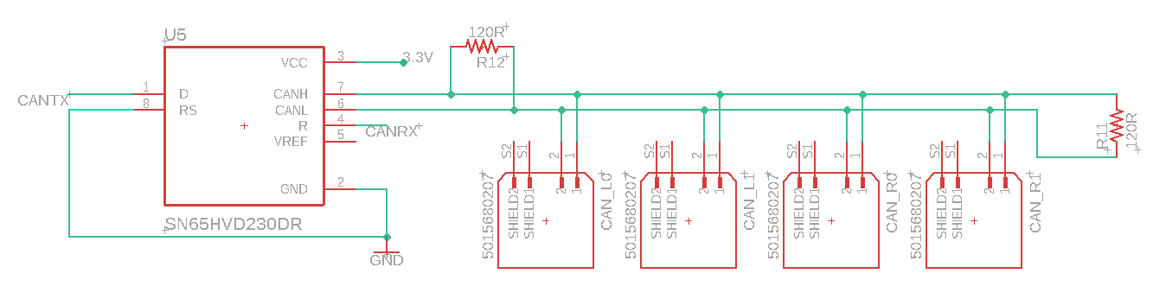
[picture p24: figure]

- Strain gauge amplifier (INA125U): This amplifier boosts the torque sensor signal output. The INA125UA is also compatible.

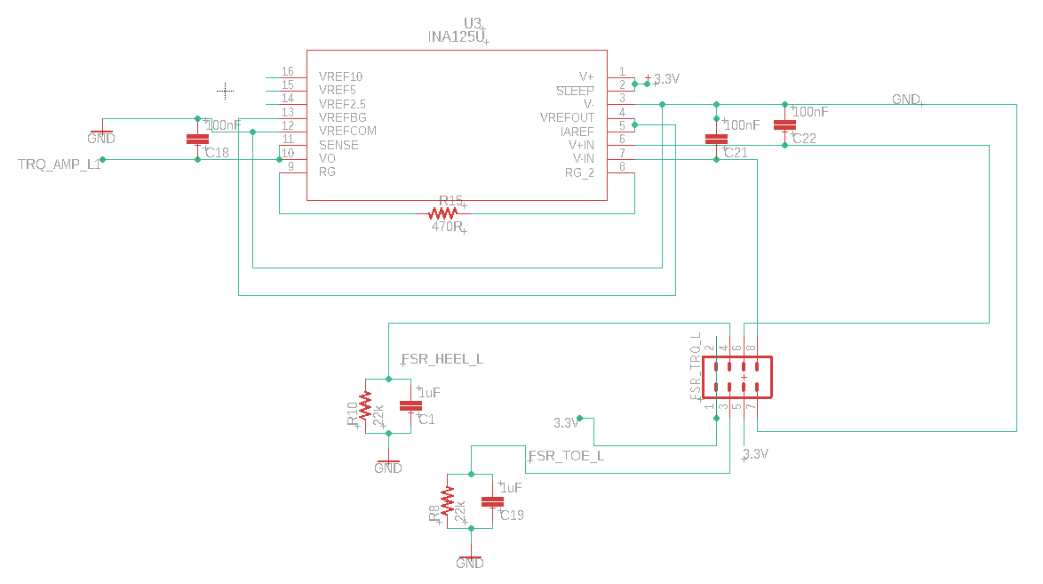
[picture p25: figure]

Other components/subsystems:

- Battery power monitor (INA219)
- RGB LEDs (2SJ305TE85LF)

While the OpenExo is fully functional without these subsystems, certain code changes may be required if they are omitted from the board.

# Ordering the PCB

All necessary resources to order the OpenExo PCB are provided (NAU_OpenExo_PCB_Files.zip). If modifications are needed, follow these instructions to generate the required files for a PCB manufacturer.

## Files needed:

- Gerber file (.zip)

This file contains the board design information necessary for PCB manufacturing and can be generated using PCB design software. The NAU OpenExo PCB was designed with Autodesk EAGLE 9.6.2. To generate the Gerber file in EAGLE, load the “.brd” file, switch to “board view”, select “File > Generate CAM data”, click on “OK”, and save the zip file.

- BOM file (.csv)

The Bill of Materials (BOM) lists all electronic components to be placed on the PCB, facilitating communication between the designer and manufacturer.

- CPL file (.csv)

The Component Placement List (CPL) describes the location and orientation of each surface-mount technology (SMT) component on the PCB, guiding the pick-and-place machine.

## PCB manufacturer:

The NAU OpenExo PCB was ordered from JLCPCB (https://jlcpcb.com/), which provides component ordering services and optional PCB assembly (soldering). JLCPCB offers automated pipelines for easy BOM and CPL file generation. The required ULP pipeline can be found on JLCPCB’s GitHub repository (https://github.com/JLCPCB/jlcpcb-eagle).

## Ordering the PCB from JLCPCB

1. Create an account at JLCPCB.com
2. Select “Order now”
3. Add the gerber file (.zip)

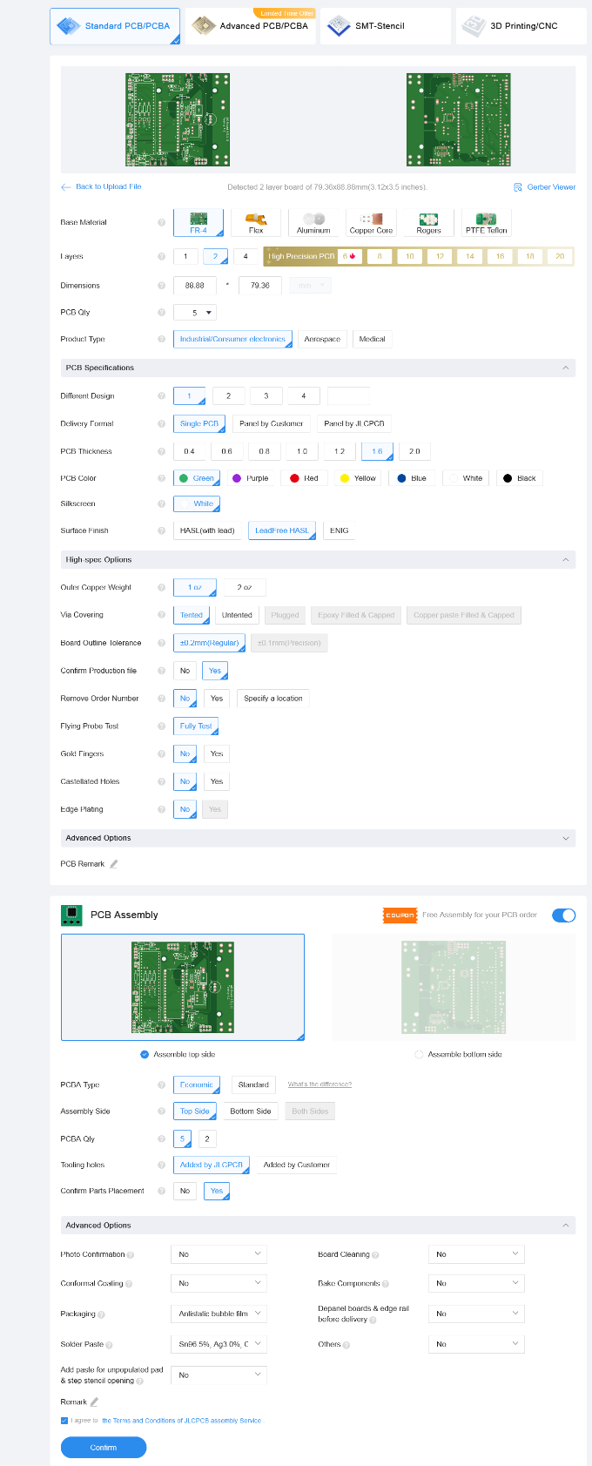
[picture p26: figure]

4. If “PCB Assembly Service” is needed, on the next pages please upload BOM (.csv) and CPL (.csv). Components not included in BOM and CPL will not be assembled onto the PCB by JLCPCB.
5. Review the order. JLCPCB may contact you to confirm the production file.

# Modifying the PCB for a Larger Battery

We currently utilize 22.2 V LiPo Batteries (https://www.amazon.com/HRB-1800mAh-Helicopter-Airplane-Multicopter/dp/B088QXJNJV/) to power our device. While perfectly functional, these batteries are the limiting factor for device operation time. If you wish to utilize a battery that would lead to a longer operation time, such as Inspired Energy’s 28.8 V Li-Ion Battery (https://www.inspired-energy.com/products/details/3/209-ph3059hd29), you will need to swap out Capacitor C16 (red box) with one of a higher capacitance (https://www.mouser.com/ProductDetail/Vishay-BC-Components/MAL217250471E3?qs=vvQtp7zwQdMjYJ1hQJzD0Q%3D%3D). If you do swap batteries, you may need to modify connectors and the design of the battery/PCB casing to accommodate this.

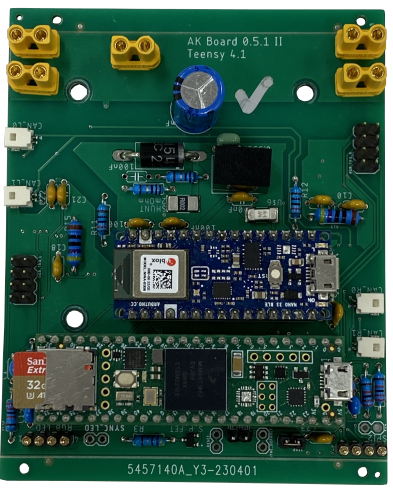
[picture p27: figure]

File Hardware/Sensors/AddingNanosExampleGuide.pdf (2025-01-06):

## Adding New Sensors

## Contents

## Introduction

This document will walk the reader through the process of adding new sensors to the OpenExo system via an example using gyroscopic data from Arduino Nanos. These Nanos will send their gyroscope data via I2C to the Teensy 4.1 located on the exoskeleton’s PCB. After reading this document the reader will gain familiarity with how to wire a new sensor to the exoskeleton, establishing communication between the sensor and the Teensy, and how to handle communication when the sensor needs to send data that is specific to its side of the exoskeleton.

## Justification for the Sensors Being Added

The sensors being integrated here are two Arduino Nano 33 BLE Sense Rev 2s. These Nanos will be mounted on the carbon fiber uprights on either side of the exoskeleton and will send angular velocity data using the Nanos’ onboard gyroscope. The Nanos will send that data via I2C to the Teensy 4.1 on the PCB of the exoskeleton. To make use of this data, code will be added to the Controller.cpp and Controller.h files in the software. The code in these two files will allow the exoskeleton to access this data and use it to calculate motor commands. However, using the data to calculate motor commands will be omitted here to keep the guide simple and relevant to the task of connecting new sensors. How the data factors into the motor commands is up to the reader to determine, as it will vary based on sensor type and desired torque profile.

## I2C Considerations

The communication protocol used here is I2C, facilitated by the Arduino Wire library. A complication that arises when using the Wire library is that it expects the data being sent and received to be formatted as bytes. Thus, we’ll need to convert the float values that we get from the gyroscopes to a vector of bytes, send that vector of bytes via the Wire library, and then convert the vector of bytes back to float values. The details of this process will be covered below.

## Wiring

This section outlines the process of finding available pins on the PCB and wiring the sensors appropriately.

## Finding Pins

Below is an overhead-view schematic of the exoskeleton’s PCB with the available pinouts annotated.

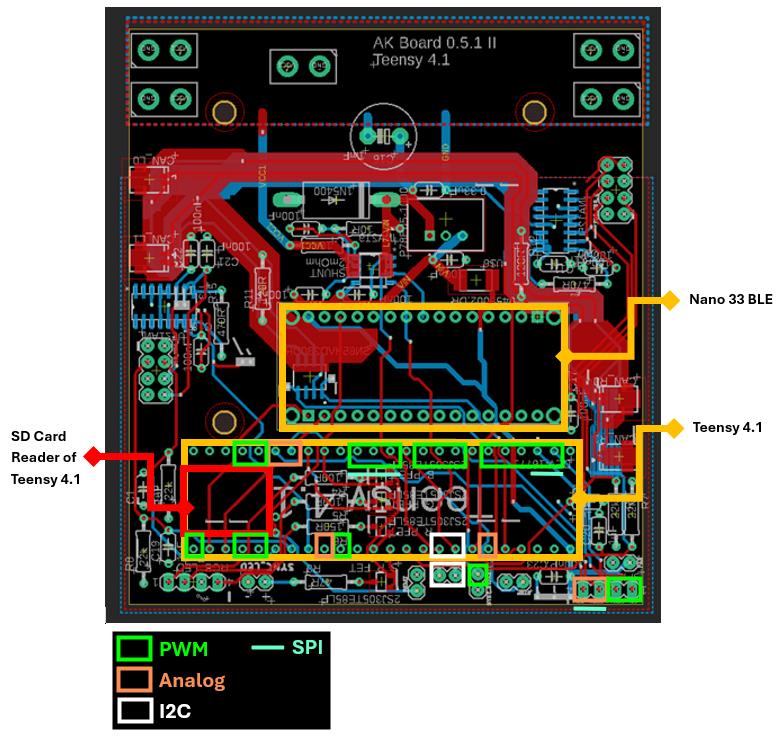
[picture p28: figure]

Figure 1: PCB Layout
As mentioned previously, the Nanos will be communicating with the Teensy via I2C. Thus, we’ll need to select one of the available I2C pinouts labeled in the image above. In this case, we will use the two I2C pins outlined on the Teensy board itself (rather than on the PCB). Referencing PJRC’s pinout diagram for the Teensy 4.1, (https://www.pjrc.com/store/teensy41.html) we find that the two pins just selected correspond to pins 18 and 19, with pin 18 corresponding to the SDA line and pin 19 to the SCL line (please review the basics of I2C communication if you are unfamiliar with that terminology). Furthermore, we again reference PJRC’s pinout diagram to find the 3.3V and GND pins. Make sure to double check “Board.h” in the software to ensure these pins are available for use.
Similarly, we must now to determine the pins to be used on the Nano side. Referencing the pinout diagram for the Arduino Nano 33 BLE Sense Rev 2, (https://store-usa.arduino.cc/products/nano-33-ble-sense-rev2) we find that the A4 and A5 pins correspond to SDA and SCL respectively. Furthermore, we again note the location of the VIN and GND pins.

## Soldering

Now that we know the location of the pins we need, we can solder wires accordingly. Below are images of the soldered wires. Note that the wires change color between the PCB and the nano. On the PCB, grey and purple correspond to ground and power respectively, and the green and yellow wires are for the I2C lines. On the Nanos, red and black correspond to power and ground while green and yellow again are the I2C lines.

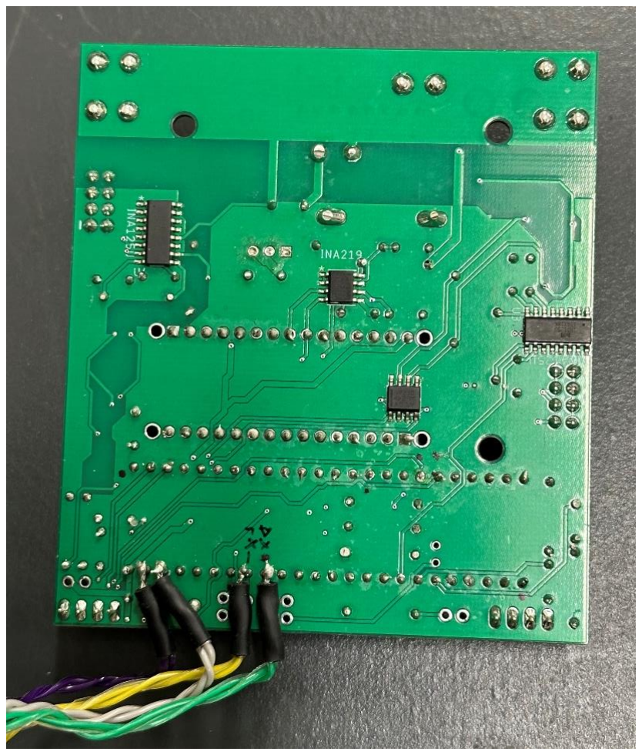
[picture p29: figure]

Figure 2: PCB Wiring

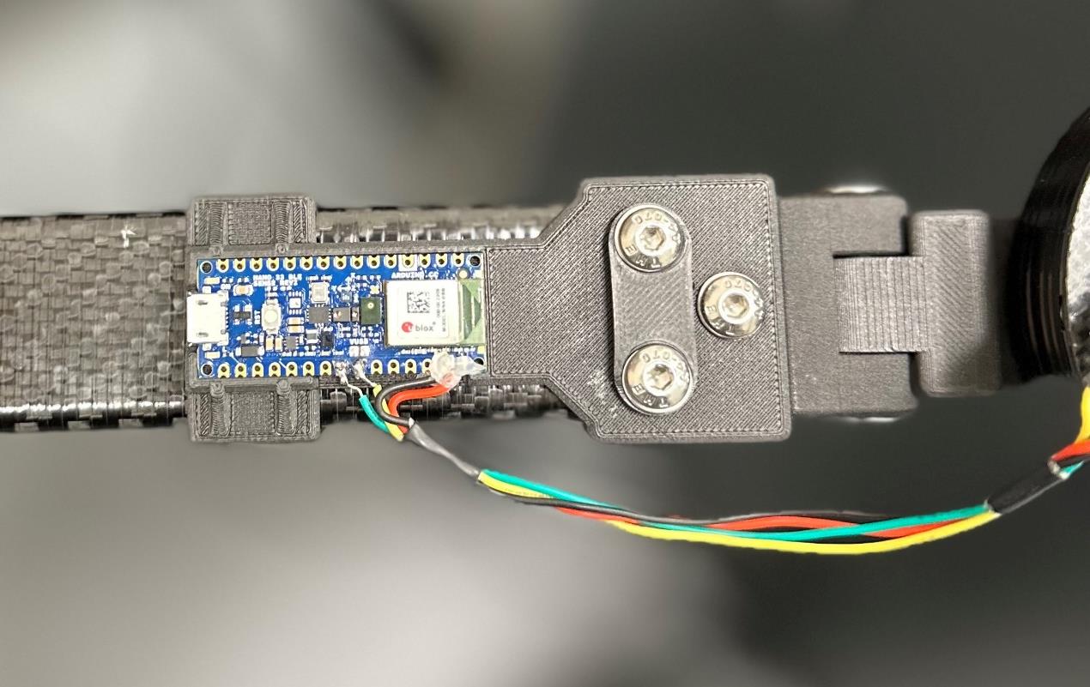
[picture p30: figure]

Figure 3: Nano Wiring
In the image, the PCB has two of each wire on each pin. This is because, as mentioned previously, there are two Nanos, one for either side of the exoskeleton. I2C can handle multiple devices on the same I2C line, provided the devices (i.e., the Nanos) have different addresses. With the Nanos, we can manually set the address in the code. However, if the reader wishes to use a different sensor, they should ensure that they can either set the I2C address manually, or that the two devices they are using have different addresses. If there is only one device on the I2C line however, this is not an issue.
It is good practice to use a multimeter to verify that everything is wired properly and that there are no shorts.

## Code

In this section, we’ll write a basic script to verify that everything is working properly. If the reader is following along, it is assumed at this point that they have downloaded OpenExo. The code we’ll be writing will be located in:
OpenExo/ExoCode/src/Controller.cpp (and Controller.h).
It is also assumed that the reader has already written the code to implement their own controller, for straightforward instructions for doing so, see: OpenExo/Documentation/AddingNew/AddingNewController.md.

## Nano Code

First, we’ll write the code that will go on the Nanos. Since we are using I2C, we’ll need to decide which device will be the primary. In this case, the Teensy will be the primary and the Nanos will be the secondary (peripherals).
With that decided, we’ll begin writing the code for the Nanos. I will only outline the code for the Nano on the left leg of the exoskeleton, as the code for the right Nano will be identical except in a few cases. When the code is side-specific, this will be explicitly highlighted.
To begin, we’ll need to make two new Arduino files (one for each Nano) and name them something appropriate. For example, in this instance we named them “nanoGyroLeft.ino” and “nanoGyroRight.ino”.
Global Variables
Now that the files are made, we’ll want to include the Wire library so that we can use I2C (Line 2 below). Next, we’ll define the I2C addresses of the Nanos. They need to be different so the Teensy can tell them apart. It can be any number, but I’ll use 8 for the right Nano and 9 for the left (Line 4 below). Furthermore, since I’m using the Nano 33 BLE Sense Rev 2, I’ll need to include the library that allows me to make use of the on-board gyroscope (<Arduino_BMI270_BMM150.h>; Line 6 below).

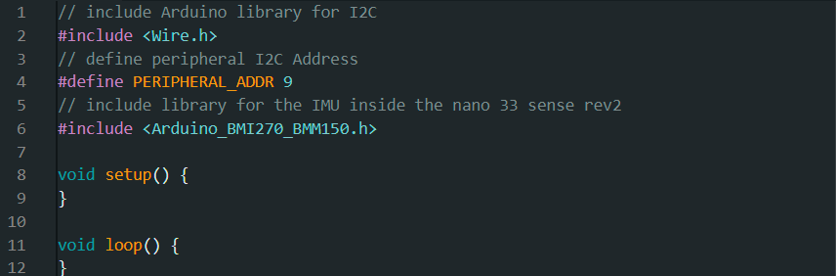
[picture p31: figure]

Next, we’ll want to establish a union to store the data we want to send (see AddingNewSensor.md in the OpenExo documentation for more information on Unions). A union is used because it allows the same data to be accessed in different ways. In our case, we get float data from the gyroscope, but we need the data to be formatted as a vector of bytes to send it over I2C. So, we’ll use a union to enable us to do so easily. The union is initialized globally and the syntax for doing so is shown in the image below.

Float-type data consists of four bytes. As such, we will need to initialize our byte-type variable as a vector of four bytes so that it can properly store the gyroscope data, hence the
[4] at the end of “angularVelBytes”.
Void Setup()
Now we’ll move into void setup(), shown below. We will initialize I2C communication with “Wire.begin(PERIPHERAL_ADDR)”. Remember that we defined PERIPHERAL_ADDR above. It is 8 for the right Nano and 9 for the left. Specifying the address tells the wire library that the device is a secondary, not the primary.
“Wire.onRequest(sendEvent)” tells the Nano to execute the function “sendEvent()” when it receives a request from the Teensy. Send Event will be defined last in the code. “IMU.begin()” simply initializes the IMU on-board the Nano.

Void Loop()
Here, we will repeatedly record the gyroscope reading about the z-axis into the float-type variable in the union.

Void sendEvent()

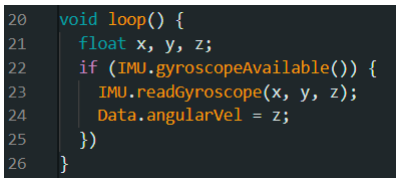
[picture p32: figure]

Finally, we’ll define the function used to send our gyroscope data upon request of the Teensy. As mentioned previously, we’ll need to send the data as a vector of bytes. Because we used a union, this is as easy as simply accessing the byte-type variable of the union that we had just stored our gyroscope reading into. We also need to specify the size of the data being sent, which we established previously is four bytes.

## Teensy Code

In this section, we will cover the code to be uploaded to the Teensy 4.1. What we’ll need to do on the Teensy is receive the data coming via I2C from the Nanos and convert it back to float data. Additionally, since the exoskeleton runs a unique instance of the code for the left and right side, we’ll want to ensure that we’re receiving the data from the Nanos in a manner that agrees with that structure. This will be elaborated upon below. Again, it is assumed that the reader has already written the outline for their own controller based on the instructions in AddingNewController.md.
First, the reader will want to open Controller.h and Controller.cpp and navigate to the portions of code relevant to their controller. In my case, the controller I created is called “Angle” as can be seen in the snippet of code from Controller.h below, which is where we will begin.
Controller.h
The reader’s controller should look something like the image below.

To start, we’ll define a union identical to the one on the Nanos.

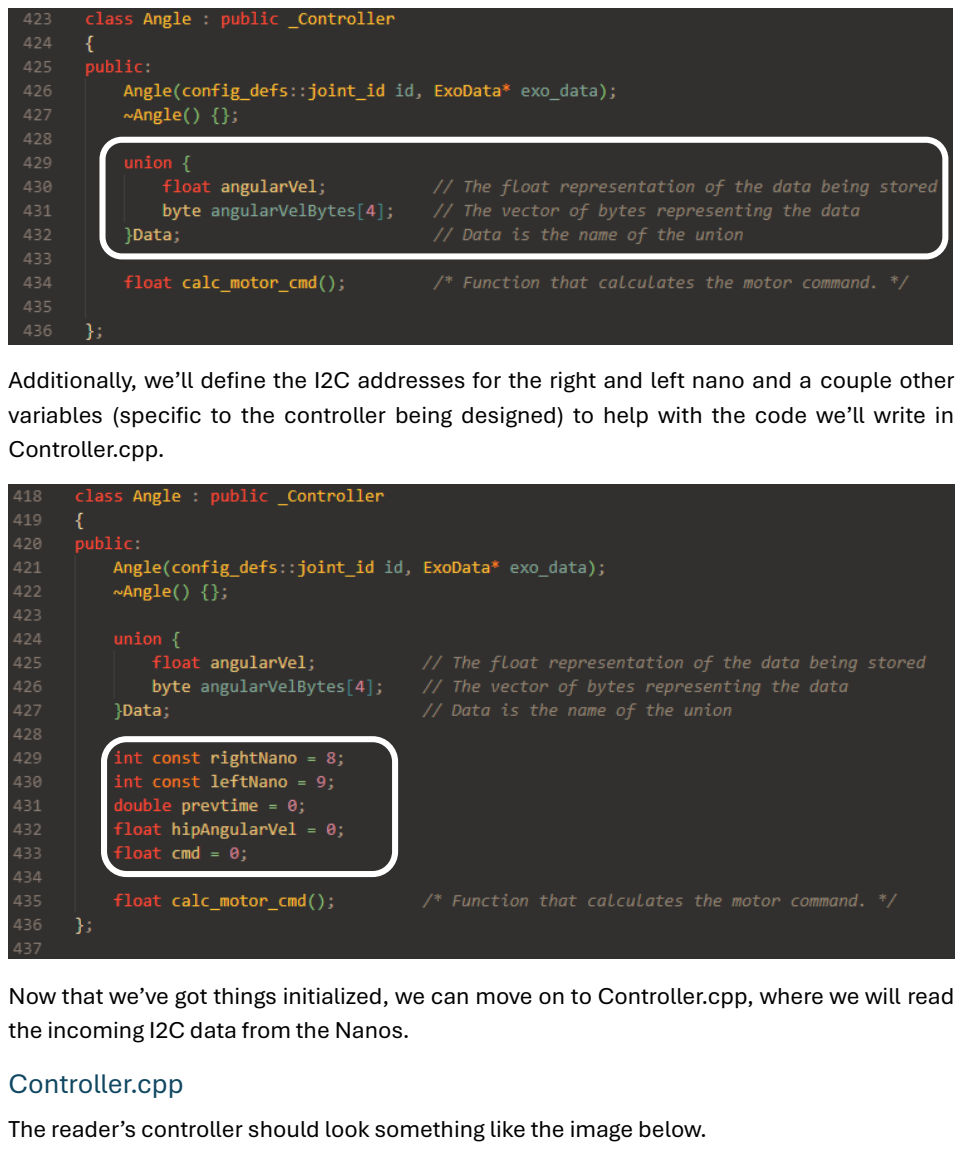
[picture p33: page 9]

Additionally, we’ll define the I2C addresses for the right and left nano and a couple other variables (specific to the controller being designed) to help with the code we’ll write in Controller.cpp.

Now that we’ve got things initialized, we can move on to Controller.cpp, where we will read the incoming I2C data from the Nanos.
Controller.cpp
The reader’s controller should look something like the image below.

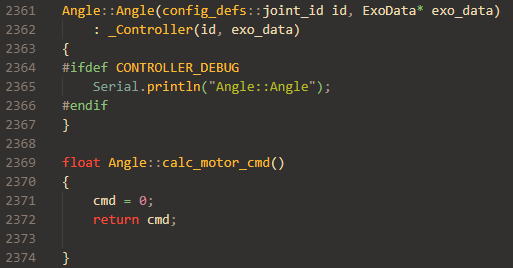
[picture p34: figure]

Within calc_motor_cmd() is where we will write our code to receive the angular velocity data from the Nanos. Notice that the cmd variable is set to zero at the moment. This is because we do not want to send torque to the motors. The motors should not run unless connected to the python GUI, which we will not be doing here, but to ensure that nothing unexpected happens it is best to not alter this variable for the time being.
We’ll start by adding if statements so that we can have the right Nano’s data be received only for the instance of code running for the right side of the exoskeleton and similarly for the left Nano. Essentially, what we will be saying is “if the current instance of the code is for the left side of the exoskeleton, then pull data from the left nano. If the current instance is for the right side, then pull data from the right Nano.”

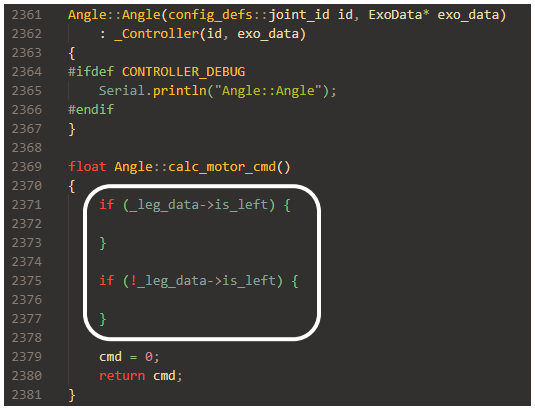
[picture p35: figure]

This is the only place we’ll need to specify the side. We will not be writing a full controller here, but if we were, the code corresponding to the calculation of the motor command would be written outside of the if statements. Again, the if statements are simply to ensure that the data from the left Nano is read by the left-side instance of the code and similarly for the right Nano.
Now we’ll fill out the if statements with the code to read from the Nanos.

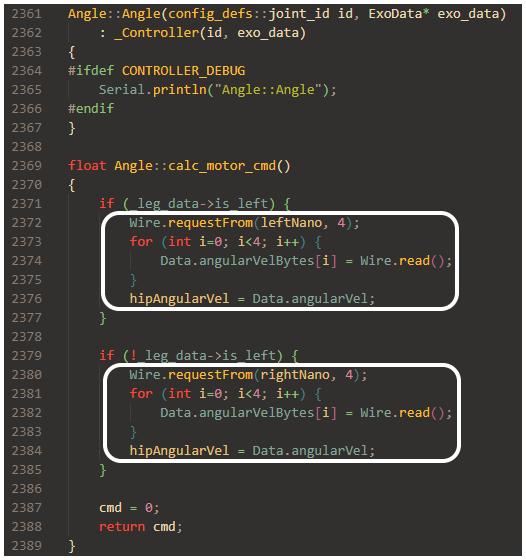
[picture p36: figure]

As can be seen in the image, we have the Teensy send a request to the Nanos for data with a size of four bytes (Line 2372). Immediately after, the Teensy then reads the incoming bytes and one-by-one appends them to the vector of bytes that we had defined previously in the union in Controller.h (Lines 2373-2375). Once all four bytes have been appended, we then set a variable equal to the float version of the data just received (Line 2376).
We will now use serial prints to verify that the data is being received properly. It is worth double checking that the reader’s active controller set in the SD card on the Teensy is the one they intend.

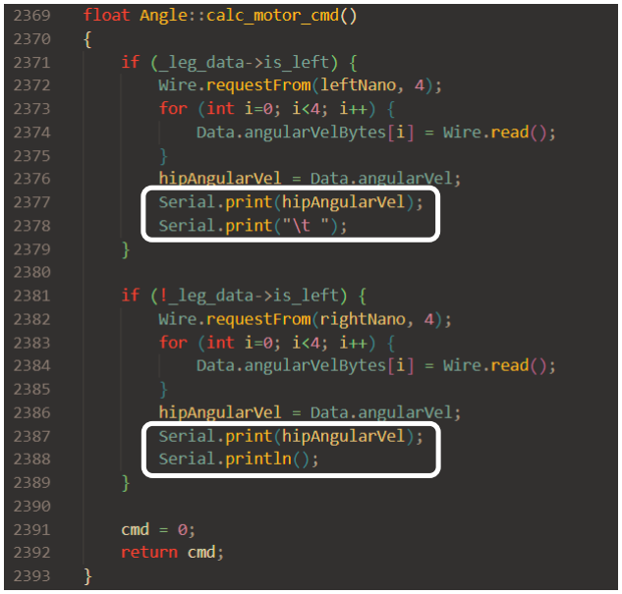
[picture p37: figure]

Because the serial prints are within the if statements, we will get a reading from the right and left Nano despite using only one variable; it’s simply that in the code running for the right side of the exoskeleton that variable is associated with the data coming from I2C address 8, and for the left side it’s associated with I2C address 9. And because the code runs for one side and then the other, we’re able to format the serial prints as seen in the image. This particular snippet of code hopefully gives the reader a better understanding of how the exoskeleton runs.
Because continuously requesting and reading data from the Nanos can cause some lag in the exoskeleton when connected to the GUI, we will decrease the rate at which the Teensy samples the Nanos with the following addition (Line 2371 below).

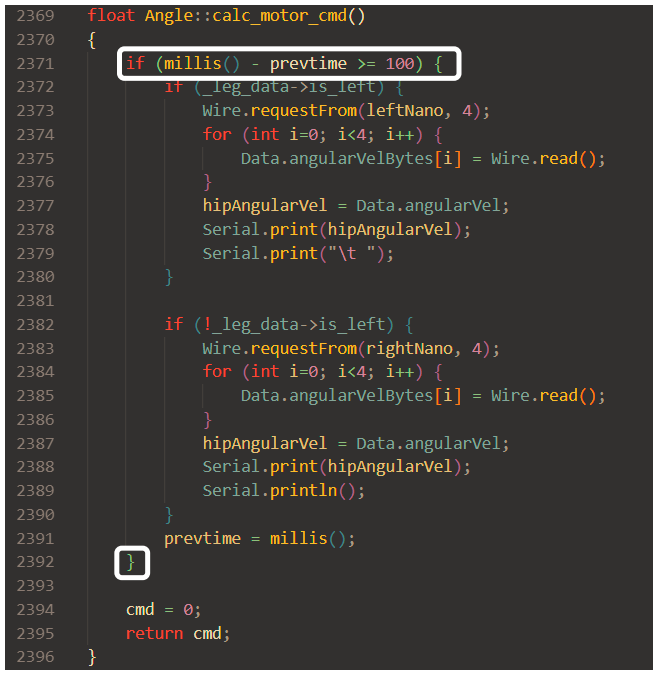
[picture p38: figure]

## Conclusion

In summary, we have added two new sensors, wired them, programmed them to send data over I2C, programmed the exoskeleton to receive that I2C data, and have written the code in such a way that the sensors send their data to their respective side-specific instance of the code.
Hopefully it is easy to see how this can be further extended to use this data to send motor commands (the variable can be treated as any other variable, such as FSR data in the Franks_Collins controller).

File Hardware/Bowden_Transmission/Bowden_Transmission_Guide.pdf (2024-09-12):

## Table of Contents

## Purpose:

The purpose of this document is to guide users on constructing a Bowden-transmission system for OpenExo, with the goal of providing a base from which researchers can innovate on end-effector design. This guide, and its associated designs, centered on interfacing with AK-series motors, of which three different sizes can be used (AK60V1.1, AK70, and AK80). For simplicity, this guide will cover the construction using the AK60V1.1 motor, but the process is identical for the other sizes as well (with small variations in components used to account for difference in sizing and the torque generation capacity between motors). Future work will include designs for even more of these motors as well as motors from other companies (i.e., Maxon).

## Fabrication of Parts:

Most of the components for this Bowden-transmission system are 3D printed. In addition to these, there are two machined components, the sprocket and the cable-chain interfaces, which will need to be manufactured in-house or by a 3rd party. This section aims to provide an outline for the fabrication of these parts.

## 3D Printed Components

If you do not have a 3D printer, it is possible to have a company, such as Protolabs Network, (https://www.hubs.com/3d-printing/plastic/nylon/carbon-filled-nylon/) print these components for you. While we use, and recommend, Onyx material for our prints, you are more than welcome to use alternative materials. Below is a list of the 3D printed components to this system, the design files for each of these can be found in the “Parts” folder associated with this document.

- Cartridge
- Belt-to-Motor
- Back Cover
- Strain Relief Shell
- Motor Cable Strain Relief
It should be noted that some of the sizing and spacing of these components vary depending on the motor (i.e., AK60V1.1 vs. AK80). It is important to print the proper size of the components for the desired motor. The files are organized such that all parts corresponding to a given motor size (e.g., AK80) are within a folder corresponding to the name of that motor. It should also be noted that there is one additional 3D printed component for the AK70 motor called “Cartridge Spacer”. This is included as the shape of the AK70 motor is slightly different compared to the other motors, which would prohibit the same general design scheme used for the other motors.
In addition to these components, there is one final 3D printed component to the system called “Strain Relief Inserts”. We print these using thermoplastic polyurethane (TPU), but feel free to use a material with similar quality if you so desire. These components are designed to reduce the strain applied to the steel-cable/Bowden-tube exit point from the 3D printed material as this was an area with a higher failure rate compared to the rest of the system.

## Machined Components

Moving on to the machined components, these consist of the sprocket and the cable-chain interface. If you have the capability, you may machine these components yourself. Otherwise, a third-party such as Xometry (https://www.xometry.com/capabilities/cnc-machining-service/?hsa_acc=3789459769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) can machine them for you. Note that there are differences in sizing for both the cable-chain interfaces and the motor sprockets depending on choice of motor (to account for differences in Motor design and the torque generating capability of the motors). Similarly to the 3D printed components, the proper sizes of these can be found in the respective motor size’s folder under the name “Cable_chain_interface_MOTORSIZE.SLDPRT” and “Sprocket_MOTORSIZE.SLDPRT.” We use 6061 T-6 aluminum for the cable – chain interface and 15-5 stainless steel for the sprocket.

## The Chains

Similar to the other components, the chains are sized based on the motors used. If you’re using the AK60V1.1 motor, you’ll need the smaller chain size which can be ordered here (https://www.mcmaster.com/catalog/130/1314/6027K71) (6mm pitch, 4mm roller diameter, and 2.8mm roller width). If ordering from McMaster Carr, the minimum length you can order is 1’ of chain. You’ll need two chains of about 6” in length, so you’ll need to size the chain yourself once you have it. You’ll also need a total of four master links, which can be ordered from the same page.
If you’re using the AK70 or AK80, you’ll need a larger chain, which can be ordered here (https://www.mcmaster.com/catalog/130/1314/6027K71) (8mm pitch, roller diameter of 5mm, and 3 mm roller width). You’ll need two chains 7” in length but again, the minimum length you can order from McMaster Carr is 1’ so you’ll need to order 2’ and size accordingly yourself. As with the AK60V1.1, you’ll need a total of four master links as well, which again can be ordered from the same page as linked above. Make sure that you order the correct size for your chain.
The sections below will assume you have the correct size and length of chain on hand.

## Construction:

The following sections will serve as a guide for the assembly of the device. It will be assumed that you have already printed and machined the components mentioned above. It may be beneficial to review all of the following sections before beginning assembly so that you know the general path before embarking. As mentioned previously, some components are sized differently depending on the motors used and thus may appear different from the parts that you have. The sizing used in the following sections is for the AK60V1.1.

## Preparing the Cartridge and Backplate

Beginning with the cartridge in which the chain and cable sit, grab the 3D printed cartridge and press the bearing into its designated slot in its center.

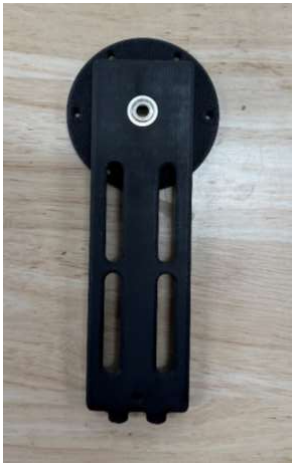
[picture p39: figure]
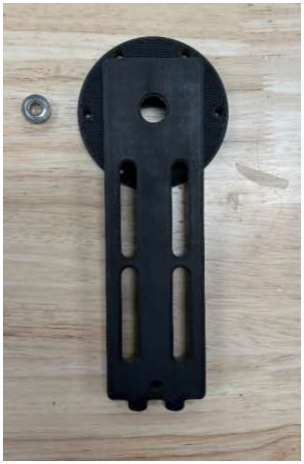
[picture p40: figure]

Next, grab the 3D printed backplate and press an M3 threaded insert into the hole in the bottom of the part as seen below. Later, a screw will pass through this insert to fasten everything together.

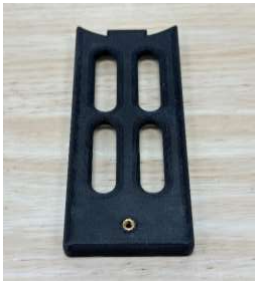
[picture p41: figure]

## Preparing the Motor and Sprocket

Now we will fasten the sprocket onto the motor. The sprocket will interface with the chain, which in turn interfaces with the cables that actuate the exoskeleton.
Grab the motor and sprocket as well as six M3x8 screws. Use the screws to secure the sprocket onto the face of the motor. The screws will pass through holes on the sprocket and will thread into the six threaded innermost holes on the motor (two of the holes are not threaded). Some of these holes may be a bit more challenging to secure as some of the sprockets teeth partially overlap with them, but with some careful effort (you may have to back out other screws to get it to sit properly) it should be possible to fasten them. Be careful not to overtighten these screws during this step as it is easy to punch into the center of the motor damaging it!

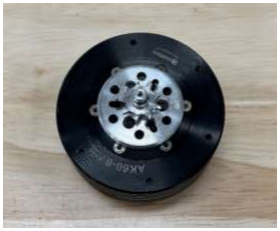
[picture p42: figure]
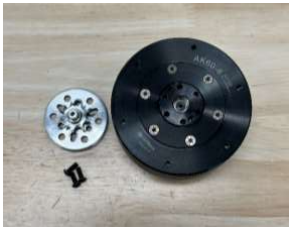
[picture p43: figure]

## Making the Chain-Cable Assembly

As mentioned previously, the chain and cable chain interface sizes will depend on motor size. As such, the components below may appear slightly different than the ones you have. Once you have the properly sized chain, remove the master links. To do so, grab a pair of pliers and use them to remove the fastener that holds the master link in place. Once the fastener is off, also remove the master link. An image with the fastener and master link removed from the chain is shown below. Make sure to do this for both sides of the chain.

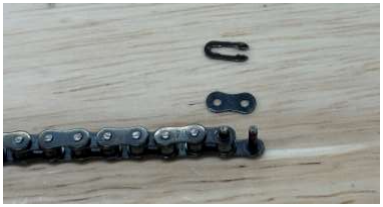
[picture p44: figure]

Once the master links are off, place the cable-chain interfaces onto the now open links on both sides of the chain. Replace the master links and their fastener over the interfaces to secure them (a pair of pliers or tweezers will be helpful during this step). With that, the chain is ready to accept the cables. Again, both sides of the chain need an interface.

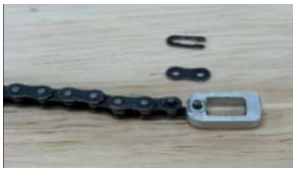
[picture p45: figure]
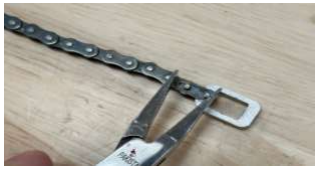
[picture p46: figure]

Next, cut cables (two for each motor, four total bilaterally) to the desired size for the user of the device. You will need to determine this length for yourself. Once cut, thread the cable through the bottom of the chain-cable interface and crimp. The process is shown below.

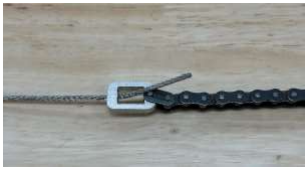
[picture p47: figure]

Once the end of the cable is crimped, slide the cable back through the interface so that the crimp sits inside the slot of the interface as seen below.

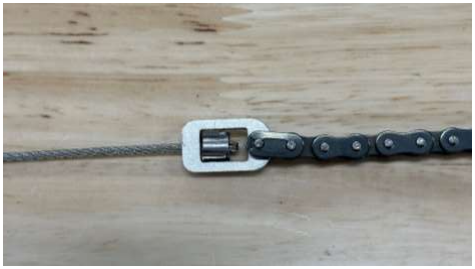
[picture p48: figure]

Repeat this with another cable on the other side of the chain.
Next, we’ll cut bowden-tubes to the needed length for the cable. Measure how long you need the tubes to be and cut using a dremel. The ends of the cable may be damaged from the cut. If so, use a belt sander (or if one is not avialbe, standard sand paper) to smooth the ends.

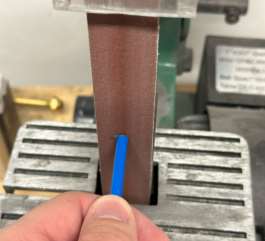
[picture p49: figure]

Further, you’ll likely need to clear out some of the interior sheathing of the bowden tube, so that the steel calbe can properly slide into the tubes. To do so, take a small hex key (or any small tool) and use it to clear out some of the interior sheathing near the end of the tube so that the cable can run freely through it. If the cable runs freely into the tube, on both ends, then it should be ready for assembly.

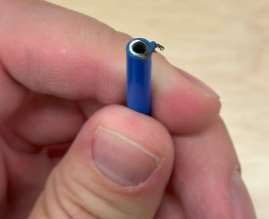
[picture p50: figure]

## Putting the Motor Assembly Together

Take the chain and cable assembly and thread the cables through the bottom two holes of the 3D printed cartridge and place the chain around the bearing in the top portion of the cartridge, as shown in the images below.

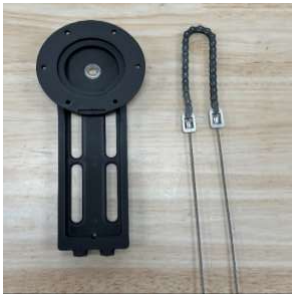
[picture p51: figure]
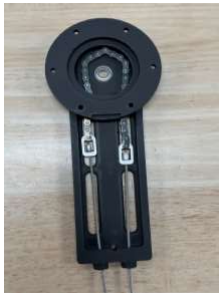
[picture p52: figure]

Place the motor onto the cartridge such that the shaft of the sprocket goes through the hole in the bearing and the chain can interface with the teeth of the sprocket. Once the motor is on, ensure that the chain is properly engaged with the sprocket by pulling on one end of the cable. You should feel the resistance of the motor as you pull. Make sure that the cable-chain interfaces are evenly aligned (relativly) within the cartridge. If they are not this can cause issues during operation where the interface runs into sprocket, potnetially damaging both and leading to device failure.

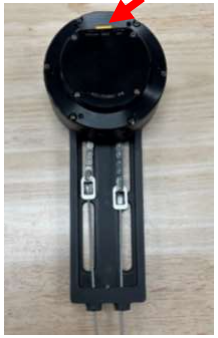
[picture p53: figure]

Once the chain is properly engaged, use four M3x10 screws to fasten the cartridge onto the motor. Ensure that the cable ports on the motor are facing upward (red arrow).

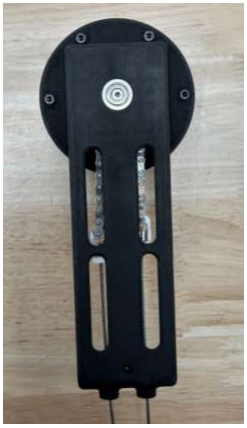
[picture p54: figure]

Thread an M3X6 screw with a washer into the threaded hole in the middle of the bearing.

Slide the Bowden tubes onto the cables and flip the motor over and set the backplate into place. Do not screw it in yet. We will first put the strain reliefs into place.

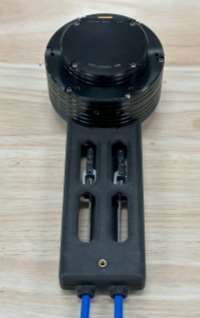
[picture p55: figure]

Slide the TPU strain reliefs over the Bowden tubes.

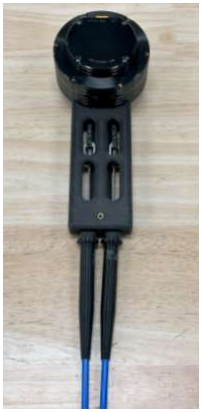
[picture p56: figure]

Slide the strain relief shell over the TPU strain reliefs and pull the TPU strain reliefs all the way to the bottom of the shell.

Slide the strain relief shell over the cartridge so that the holes align.

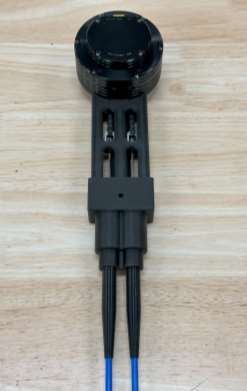
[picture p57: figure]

Flip the motor over and use an M3x30 screw to fasten the strain relief shell to the cartridge.

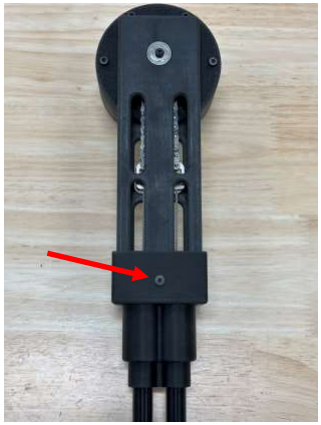
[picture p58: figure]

## Preparing the Hip Belt

Using the 3D printed mount and a sharpie, mark the position of four mounting holes on either side of the belt with the Belt to Motor 3D printed piece used as reference. Try to have this aligned as straight as possible or slightly angled as that the Bowden tubes exiting the cartridge point out away from the body.

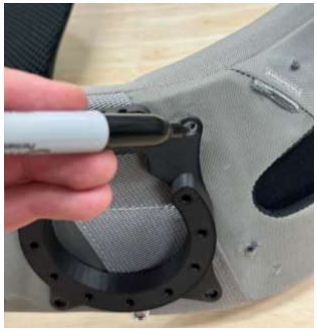
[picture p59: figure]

Use a 5mm bit to drill the four mounting holes whose positions you just marked

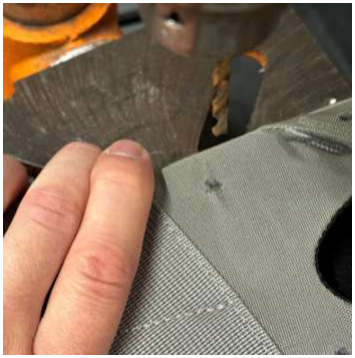
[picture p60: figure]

Press four M5x20 screws through the holes on either side such that the threaded ends stick out the back side of the belt.


## Mounting the Motors onto the Belt

With the belt now ready to accept the motors, screw the 3D printed mounts onto the motors as shown

Mount the motors onto the belt using the screws you set into the belt and M5 lock nuts


And with that, the assembly of this belt-side Bowden-transmission system is finished. We leave the end-effector side design and assembly up to you to innovate and utilize as you see fit!

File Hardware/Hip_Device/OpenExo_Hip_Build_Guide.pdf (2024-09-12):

## PURPOSE

This document serves as a guide for the construction and assembly of the NAU Biomechatronics Lab’s OpenExo Hip Device. Pictures and supplemental videos are provided to help visualize the steps required to manufacture every component and fully assemble the device. In addition to this documentation, we have provided a complete Bill of Materials (BOM) with information on where to purchase the needed parts (and expected cost), and SolidWorks design files for all the needed components.

Table of Contents

PURPOSE | 1
PARTS/MATERIALS REQUIRED | 4
TOOLS REQUIRED | 4
PPE | 4
General Tools | 4
Tools for Electrical Components | 5
PRINTING REQUIRED PARTS | 5
Filament Used | 5
Carbon Fiber Reinforcement | 5
List of all Printed Components | 5
Thigh Cuffs | 6
1. Sizing | 6
2. Printing | 10
3. Assembly | 12
MAKING YOUR OWN INSOLES (optional) | 20
PREPARING THE HIP BELT | 22
Making the Mounting Plates | 22
1. Cutting the Plastic | 22
2. Drilling Mounting Holes | 23
3. Thermoforming | 24
4. Mounting the Plates to the Belt | 25
Mounting the Battery & PCB Casing | 27
1. Printing | 28
2. Mounting | 28
MANUFACTURING THE CARBON FIBER PARTS | 30
1. Machining the Parts for Yourself | 30
2. Third-Party Machining | 31
3. Drilling Mounting Holes into the Carbon Fiber Tubes | 31
OBTAINING THE MACHINED ALUMINUM PARTS | 33
ASSEMBLING MACHINED COMPONENTS | 33

### 1. Motors onto Belt | 33 2. Attaching the Uprights to the Motors | 37

ELECTRICAL COMPONENTS | 40

### 1. Assembling the CAN Wire | 40 2. Preparing the FSRs | 45 3. Wires for Connecting the FSR to the PCB | 51

### 4. Wiring the Power Switch | 56 5. Tapping Holes for the Battery Connector | 59 6. Soldering the Status LED | 60 7. Making the Battery-to-Motor Power Cable | 62 8. Configuring the Motors | 63 9. Making the Connections | 67

ASSEMBLING THE PCB COVER | 72
PADDING FOR ADDITIONAL COMFORT | 75

## PARTS/MATERIALS REQUIRED

This build contains 3D printed parts, machined carbon fiber and aluminum parts, a prefabricated hip belt, and various electrical components including motors, wiring, and a custom printed circuit board (PCB, information on which is include in supplemental documentation). A bill of materials (BOM) is provided which outlines all the necessary materials and fasteners (tools not included). The BOM also specifies the price of every component at the time of purchase, as well as where each component was purchased.

Worth noting in the BOM are the carbon fiber plates and tubing. These materials do not need to be purchased directly if you wish to have a third party manufacture them for you. In our case, we manufactured these components ourselves. If you would like your own tools for fully manufacturing all the components, you will need a CNC, (https://toolstoday.com/stepcraft-3d-600-cnc-system.html) a 3D printer, (https://markforged.com/3d-printers/mark-two) a drill press, (https://www.amazon.com/WEN-4208T-2-3-Amp-5-Speed-Benchtop/dp/B08ZVT5JKC?hvadid=580530431901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) and a Dremel. (https://www.amazon.com/Dremel-4000-4-34-Variable-Rotary/dp/B00LUU2XFO?sp_csd=d2lkZ2V0TmFtZT1zcF9hdGY)

Also worth noting are the three items under “Externally Manufactured Parts.” These include aluminum adduction/abduction blocks (made of 7075 aluminum), which serve to allow out-of-plane motion on the hip belt, as well as a custom PCB used to control the exo. Information on where these were externally manufactured are available later in this document and in the BOM.

## TOOLS REQUIRED

## PPE

For certain aspects of this build, adequate personal protective equipment (PPE) will be necessary. Below is a list of the minimum required PPE.

1) Safety glasses (https://www.amazon.com/BK310AF-Polycarbonate-Anti-Fog-Safety-Non-Slip/dp/B009A658JS?s=industrial)
2) Respirator with P100 Filters (https://www.3m.com/3M/en_US/p/dc/v000152049/?gf=true&price=list-low) (for machining carbon fiber)
3) Long sleeve shirt (for working with carbon fiber)
4) Ear protection (https://www.amazon.com/TICONN-Reduction-Protection-Concentration-Construction/dp/B0BGXKNQTQ?s=industrial&sp_csd=d2lkZ2V0TmFtZT1zcF9hdGY) (earmuffs or earplugs)
5) Heat resistant gloves (https://www.amazon.com/Ove-Glove-Superior-FLAME-Protection/dp/B0797DTFLM?s=industrial) (for thermoforming)

## General Tools

1) Metric nut driver set (https://www.amazon.com/P-I-T-3-5-inch-ightening-Loosening-Fasteners/dp/B0CRBBP2GF?s=industrial&sp_csd=d2lkZ2V0TmFtZT1zcF9hdGY)
2) Metric hex keys (https://www.amazon.com/LOZAGU-35-Piece-Standard-0-7mm-10mm-Vanadium/dp/B0CFHWB2H1?s=industrial&sp_csd=d2lkZ2V0TmFtZT1zcF9hdGY)
3) Torx drivers (https://www.amazon.com/SUNHZMCKP-12-Piece-Screwdrivers-Steel%EF%BC%8CT5-T40-Set%EF%BC%8CProfessional/dp/B09WD3NGTL?s=industrial&sp_csd=d2lkZ2V0TmFtZT1zcF9hdGY)
4) Drill (https://www.amazon.com/Cordless-Drill-Driver-Bare-18-0V/dp/B00I3MMYVU?hvadid=693363057790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) or drill press (https://www.amazon.com/WEN-4208T-2-3-Amp-5-Speed-Benchtop/dp/B08ZVT5JKC?hvadid=580530431901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) with drill bits (https://www.amazon.com/COPOUIXR-Cobalt-1-5mm-6-5mm-Material-13-Piece/dp/B0B8WYPBMF?s=industrial)
5) A set of files (https://www.amazon.com/Premium-Forged-Precision-Triangle-Half-round/dp/B083P4VQFG?sp_csd=d2lkZ2V0TmFtZT1zcF9hdGY) or sandpaper (https://www.amazon.com/Sandpaper-Assortment-9x3-6-Automotive-Sanding/dp/B074VYL3M6?sp_csd=d2lkZ2V0TmFtZT1zcF9hdGY)
6) Dremel with cutting disks (https://www.amazon.com/Dremel-4000-4-34-Variable-Rotary/dp/B00LUU2XFO?s=power-hand-tools&sp_csd=d2lkZ2V0TmFtZT1zcF9hdGY)
7) Tile saw (https://www.harborfreight.com/10-amp-7-in-wet-tile-saw-with-sliding-table-64683.html?campaignid=12144821732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) (a table saw, (https://www.homedepot.com/p/RYOBI-13-Amp-8-1-4-in-Compact-Portable-Corded-Jobsite-Table-Saw-No-Stand-RTS08/309412837?locale=en-US&pla&gad_source=1&gclsrc=aw.ds) circular saw, (https://www.homedepot.com/p/DEWALT-20V-MAX-Cordless-6-5-in-Sidewinder-Style-Circular-Saw-Tool-Only-DCS391B/203164241?locale=en-US) or jig saw (https://www.amazon.com/DEWALT-DCS334B-Brushless-Tool-Only/dp/B07JPFHQKG?hvadid=693128203622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) also works) – for cutting carbon fiber
8) Tape (gorilla or something comparable)
9) Scissors
10)CNC (https://toolstoday.com/stepcraft-3d-600-cnc-system.html) (optional if parts are externally manufactured)

## Tools for Electrical Components

1) Soldering iron (https://www.uline.com/Product/Detail/H-10799/Anti-Static-Equipment/Weller-Soldering-Station?pricode=WC4573&gadtype=pla&id=H-10799&gad_source=1)
2) Solder
3) Heat gun (https://www.amazon.com/SEEKONE-Heat-Gun-Hot-Air/dp/B078S5QMFG?hvadid=616863312459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)
4) Wire stripper (https://www.digikey.com/en/products/detail/tempo-communications/PA1161/461371)
5) Wire cutter (https://www.grainger.com/product/39AN55?gucid=N:N:PS:Paid:GGL:CSM-2295:4P7A1P:20501231&gad_source=1&gclsrc=aw.ds)
6) Utility knife (https://www.amazon.com/24Pack-Utility-Retractable-Compact-Extended/dp/B08H7XQZZ2?s=industrial&sp_csd=d2lkZ2V0TmFtZT1zcF9hdGY)
7) Crimping Tool (https://www.digikey.com/en/products/detail/molex/0638191500/1832244)
8) Helping Hands (https://www.amazon.com/Helping-Soldering-Workshop-Non-slip-Weighted/dp/B07MDKXNPC?s=hi&sp_csd=d2lkZ2V0TmFtZT1zcF9hdGY)
9) Tweezers (https://www.amazon.com/kaverme-Anti-Static-Electronics-Laboratory-Jewelry-Making/dp/B0BNNGC3Q2?sp_csd=d2lkZ2V0TmFtZT1zcF9hdGY)

## PRINTING REQUIRED PARTS

## Filament Used

The filament we use is Markforged’s Onyx. (https://markforged.com/materials/plastics/onyx) For all printed parts, we used the Markforged Desktop Series. (https://markforged.com/3d-printers/mark-two) If you do not have access to one of these (or a similar type of printer), Protolabs (https://www.hubs.com/3d-printing/plastic/nylon/carbon-filled-nylon/) is a company that can print them for you. Important to note though is that some of the printed parts include carbon fiber reinforcement (listed below), which at the time of writing this document, is not an option with Protolabs. The carbon fiber reinforcement is not required for the function of the device, but its absence may reduce the durability of those parts.

## Carbon Fiber Reinforcement

Many of the printed parts in this build use carbon fiber reinforcement to increase strength while minimizing weight. These parts include:

- thighCuffFront.SLDPRT
- cuffSliderTop.SLDPRT
- cuffSliderBottom.SLDPRT

Further specification of the CF reinforcement will be provided in the “Thigh Cuffs” section.

## List of all Printed Components

Below is a list of the printed components used in this build, as well as how many of each you will need. These components are contained in the “Part Files for 3D Printing” folder. Prior to printing components which have carbon fiber reinforcement, review the “Quad Cuffs” section where a guide for how much reinforcement to use is provided.

- (1x) electronicsBoxBackPlate.SLDPRT
- (1x) electronicsBoxBatteryCover.SLDPRT
- (2x) cuffSliderBottom.SLDPRT
- (2x) cuffSliderTop.SLDPRT

- (4x) heelPuck.SLDPRT
- (1x) holeTemplateForStrut.SLDPRT
- (2x) boltSpportForStrut.SLDPRT
- (2x) motorToStrut.SLDPRT
- (1x) electronicsBoxControlPanel.SLDPRT
- (2x) thighCuffBack.SLDPRT
- (2x) thighCuffFront.SLDPRT
- (2x) electronicsBoxStrainReliefRight.SLDPRT
- (2x) electronicsBoxStrainReliefLeft.SLDPRT

## Thigh Cuffs

The thigh cuffs are the components of the build that interface with the users thighs, allowing for the transfer of assistance from the motors to user. These cuffs can be sized differently to fit a variety of potential users. Below is an outline of how to size, print, and assemble these components.

1. Sizing
a) To size these components, open the thighCuffFront.SLDPRT file in SolidWorks.
b) Navigate to the Configuration Tree.


c) Select the desired size. The small size will fit a slim athletic build, while the medium will comfortably fit those with a larger build. The dimensions can be checked in SolidWorks and compared with physical measurements of the user’s thigh to get a good match.
d) You can now save this as an independent file such as “XXSizeRightSide.SLDPRT” for ease.

e) Next, we’ll save the mirrored version for the other side of the leg. Save another copy of the part under the name “XXSizeLeftSide.SLDPRT.” Ensure that this is the file you’re now editing and navigate back to the feature tree.
f) Now open the Solid Bodies dropdown.

g) Reveal the hidden solid body titled “Mirror1.”
h) Now delete the first body by right clicking on it in the “Solid Bodies” dropdown and selecting “Delete/Keep Bodies.”

i) Now that this is done, again ensure that you’re editing “XXSizeLeftSide.SLDPRT” and save.
j) You now have part files of the cuff for both sides of the leg.
2. Printing
These components are reinforced with carbon fiber.
- thighCuffFront.SLDPRT
- cuffSliderTop.SLDPRT
- cuffSliderBottom.SLDPRT

As mentioned above, if you are having a third party such as Protolabs (https://www.hubs.com/3d-printing/plastic/nylon/carbon-filled-nylon/) print them for you, you will not be able to print with carbon fiber reinforcement, which may decrease the durability of the parts but should not prohibit function.

If you have access to your own printer, we have outlined the locations and quantities of CF reinforcement that you should use below. When you add the CF reinforcement, ensure that for each section you set the reinforcement geometry to “concentric.”

This can be done by selecting each blue segment in the slider at the bottom of the screen (seen below).

Thigh Cuff:

Cuff Slider (top and bottom):

fab

3. Assembly
a) Gather necessary components.
1x | XXSizeLeftSide.SLDPRT
1x | XXSizeRightSide.SLDPRT
2x | cuffSliderTop.SLDPRT
2x | cuffSliderBottom.SLDPRT
2x | thighCuffBack.SLDPRT
2x | ThighCuffReinforcement.SLDPRT
1x | Fabric (3 mm) (https://www.seattlefabrics.com/Velcroreg-Brand-Fastener-Compatible-UBL-Neoprene-by-the-Linear-Foot-starting-4500-per-linear-foot_p_843.html)
1x | Velcro with Adhesive Backer (https://www.amazon.com/Denser-Sticky-Adhesive-Fastener-Strips/dp/B07N3B36Z2?th=1)
2x | Velcro Strap (https://www.securecableties.com/18-x-2-inch-cinch-straps-5-pack)
2x | Cam Handle (https://www.mcmaster.com/5720K241/)
4x | M3 Lock Nut (https://www.mcmaster.com/90370A203/)
2x | M3X16 Button Head Screw (https://www.mcmaster.com/92095A184/)
4x | M5X12 Button Head Screw (https://www.mcmaster.com/91306A666/)
4x | M5 Lock Nut (https://www.mcmaster.com/91854A102/)
4x | M5 Washer (https://www.mcmaster.com/92334A113/)
1x | Silver Sharpie (https://www.amazon.com/Sharpie-39108PP-Metallic-Permanent-Blister/dp/B00009RAX4?hvadid=616991223281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)
1x | Scissors (https://www.amazon.com/Scissors-Professional-Tailoring-Industrial-Dressmakers/dp/B07Y2ZBSN1)
1x | Superglue (https://www.amazon.com/Loctite-1364076-Super-Squeeze-Liquid/dp/B0006HUJCQ)
1x | Drill Press (https://www.amazon.com/WEN-4208T-2-3-Amp-5-Speed-Benchtop/dp/B08ZVT5JKC?hvadid=580530431901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) or Hand Drill (https://www.amazon.com/Cordless-Drill-Driver-Bare-18-0V/dp/B00I3MMYVU?hvadid=693363057790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) with 5mm Diameter Bit (https://www.amazon.com/COPOUIXR-Cobalt-1-5mm-6-5mm-Material-13-Piece/dp/B0B8WYPBMF?s=industrial)

b) Use superglue to fasten the ThighCuffReinforcement.SLDPRT to the XXSize[Left/Right].SLDPRT. We recommend clamping/securing these parts together and letting sit until dry (we typically let it sit overnight, but two hours should suffice if
needed sooner).
c) Once the glue is dry, cut small, rectangular, sections of the hook side Velcro and stick them to the inside of XXSize[Left/Right].SLDPRT in the manner shown below.
d) Now we’ll create the padding to the cuff. Insert the fabric into the cuff and align it to fill the space. Make sure to leave the space with the slot open as this is where the strap to fasten the cuff will be fed through. Using a silver sharpie create an outline of the cuff on the fabric. Take a pair of scissors and cut the fabric along the outline. Attach the fabric to the cuff via the Velcro.


e) Place hook-side Velcro on the inner side of the thighCuffBack.SLDPRTs in the manner shown.
f) Cut and fasten a piece of fabric to the Velcro to be used as padding, similar to what you did for the front side of the cuff.

g) Algin the loop-side Velcro on outer side the thighCuffBack.SLDPRT in the manner shown. Cut out that section and attach to the outer side of the back cuff.
h) Cut the buckle off of the Velcro strap so that it looks similar to the strap below


i) Place the strap in line with the the two M5 holes in the XXSize[Left/Right].SLDPRT. Make sure that the strap extends a bit past the holes into the cuff. Using the silver sharpie, mark the hole locations on the Velcro strap as shown below. These will be where we secure the strap to the cuff.
j) Use a 5 mm diameter drill bit to cut out the holes you just marked on the Velcro Strap
k) Slide the Velcro strap through the thighCuffBack.SLDPRT as shown below, with the Velcro facing the outside of the cuff.

l) Press the M3 Lock nuts into their respective slots in the cuffSlider[Top/Bottom].SLDPRT.
m) Insert the CAM lever into the cuffSliderTop.SLDPRT and a M3X16 screw into the cuffSliderBottom.SLDPRT. [Note: The cuffSliderBottom.SLDPRT has the larger (thicker) base]

Bottom; Top

n) Press M5 lock nuts into their respective slot on the cuffSlider[Top/Bottom].SLDPRTs.

o) After placing M5 washers on each, press two M5X12 button head screws through the two holes in the cuff as shown.
p) Slide the two holes in the Velcro strap over these screws, with the strap being on the outside of the cuff

q) Fasten the cuffSliderTop.SLDPRT and cuffSliderBottom.SLDPRT to the cuff as shown (make sure to pay attention to which leg you are on).


r) The finished product is shown below. The cuff is now ready to be attached to the carbon fiber uprights once the exo is ready. When placed on, they should slide onto the upright until at a comfortable height, at which time the Cam Handle can be used to tighten the upper cuff slider, securing the cuff to the upright and preventing motion.

## MAKING YOUR OWN INSOLES (optional)

To operate the exoskeleton with intended control scheme, you will need to secure FSRs to your insoles (to be detailed later). This process can damage your insoles when trying to remove the FSRs from them. As a result, we recommend buying shoes/insoles dedicated to use with the exo, or making custom insoles to interface with the device. Additionally, if you have multiple people using the exo, it will be easier and less expensive to make a variety of insole sizes than it would to purchase multiple shoes. We have outline the steps needed to make your own insoles below.

a) Gather necessary components
1x | 6 mm Foam (https://thecosplaypros.com/products/eva-foam-sheets?variant=20494372569199)
1x | Insoles (left and right) from your own shoes
1x | Sharpie (https://www.amazon.com/SHARPIE-Black-Markers-Set-High-Quality/dp/B00006IFHD)
1x | Scissors (https://www.amazon.com/Scissors-Professional-Tailoring-Industrial-Dressmakers/dp/B07Y2ZBSN1)
b) Place the left and right insoles on the foam and trace their outline.

c) Cut out the traces you made using scissors.
d) Put the pieces of foam into your shoes to check the fit. Trim if necessary. When you are done, store these for now. The FSRs will be fastened to them during the “Electrical Components” section.

## PREPARING THE HIP BELT

The first step in this exoskeleton build will be manufacturing the components to interface with the waist belt. Here we will be preparing the hip belt to accept the motors as well as modifying the belt to accept the casing for the battery and PCB.

## Making the Mounting Plates

To mount the motors to the belt, pieces of thermoform plastic must be shaped to match the belt’s contour. This process is outlined below. A video of this process is provided here, (https://drive.google.com/drive/folders/1xL2rtUE9us9Fqm-0mg9-_RyJHOJughff?usp=drive_link) which may be easier to follow than the written instructions.
1. Cutting the Plastic
a) Gather necessary components.
1x | Hip Belt (https://www.moosejaw.com/p/osprey-womens-isoform-cm-hipbelt-23trywsfrmcmhpbltbag/23trywsfrmcmhpbltbag?sku=25482757&gad_source=1&gclsrc=aw.ds)
2x | Blank Paper
1x | PVC/Acrylic Plate (thermoform plastic) (https://www.mcmaster.com/8650K21-8650K214/)
1x | Sharpie (https://www.amazon.com/SHARPIE-Black-Markers-Set-High-Quality/dp/B00006IFHD)
1x | Dremel with Cutting Bit (https://www.amazon.com/Dremel-4000-4-34-Variable-Rotary/dp/B00LUU2XFO?s=power-hand-tools&sp_csd=d2lkZ2V0TmFtZT1zcF9hdGY)
1x | Eye Protection (https://www.amazon.com/BK310AF-Polycarbonate-Anti-Fog-Safety-Non-Slip/dp/B009A658JS?s=industrial)
1x | Respirator (https://www.3m.com/3M/en_US/p/dc/v000152049/?gf=true&price=list-low)
b) Use a piece of paper and a sharpie to trace the outline of the belt section on which you intend to place the interface. You will want as much surface area as you can get for the mounting holes. Generally, the outline should span from top to bottom of the belt and go from the front edge of the belt back to the diagonal fabric pattern on the belt (see image).


c) Transfer this outline to the piece of plastic stock that you’ll be using. Use a Dremel with a grinder bit (or any other suitable tool) to cut out the shape just traced. Wear PPE (Respirator/Eye Protection) during this step as the plastic will melt and release fumes as it is cut.
d) Repeat for the other side of the hip belt. The template you made with the blank paper will work for the other side of the hip belt but ensure that you mirror the orientation of the paper to reflect the flipped contour of the belt.
2. Drilling Mounting Holes
a) Gather necessary components. This includes printing two copies of the hole pattern template (PlasticMountTemplate.pdf)
1x | Drill (https://www.amazon.com/Cordless-Drill-Driver-Bare-18-0V/dp/B00I3MMYVU?hvadid=693363057790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) with 5.9mm Diameter Bit (or similar size) (https://www.amazon.com/COPOUIXR-Cobalt-1-5mm-6-5mm-Material-13-Piece/dp/B0B8WYPBMF?s=industrial)
2x | Cut Mounting Plates (from previous step)
2x | Printed Copy of PlasticMountTemplate.pdf
1x | Tape (https://www.amazon.com/Scotch-Writable-Translucent-Recyclable-Packaging/dp/B0CV9JV563?hvadid=693649350646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)
1x | Scissors (https://www.amazon.com/Scissors-Professional-Tailoring-Industrial-Dressmakers/dp/B07Y2ZBSN1)
b) Place and position the hole template onto the cut piece of plastic so that you have as many holes as possible on the plastic. An additional, important, requirement is to have a hole near each corner so that you can use bolts to fasten it to the belt (holes will be drilled into the belt later). If the markings on the template line up well with the four corners of the plastic, then they can be used for mounting (red arrows). If this is proving challenging, space it so that the four corners have some spacing around it and then drill similar holes in those spots (green arrows = where holes for mounting would be drilled).

c) Tape the template onto the plastic.
d) Following the template, drill the holes through the plastic mount with a 5.9mm diameter drill bit.
e) Repeat for the other piece of plastic.
3. Thermoforming
a) Gather necessary components.
1x | Heat Resistant Gloves (https://www.amazon.com/Ove-Glove-Superior-FLAME-Protection/dp/B0797DTFLM?s=industrial)
1x | Heat Gun (https://www.amazon.com/SEEKONE-Heat-Gun-Hot-Air/dp/B078S5QMFG?hvadid=616863312459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)
1x | Hip Belt (https://www.moosejaw.com/p/osprey-womens-isoform-cm-hipbelt-23trywsfrmcmhpbltbag/23trywsfrmcmhpbltbag?sku=25482757&gad_source=1&gclsrc=aw.ds)
b) Put the Hip Belt on. This will ensure that the plastic is thermoformed to the proper shape.
c) Put on the heat resistant gloves and start the heat gun. Use the gun to heat the plastic to the point where it is easy to deform.
d) Press the plastic onto belt such that it conforms to the contour of the belt. Hold in place until plastic cools enough to be stiff. Assess and adjust via reheating as needed.

e) Repeat for the other side.
4. Mounting the Plates to the Belt
a) Gather necessary components.
1x | 8mm Nut Driver (https://www.amazon.com/P-I-T-3-5-inch-ightening-Loosening-Fasteners/dp/B0CRBBP2GF?s=industrial&sp_csd=d2lkZ2V0TmFtZT1zcF9hdGY)
1x | Sharpie (https://www.amazon.com/SHARPIE-Black-Markers-Set-High-Quality/dp/B00006IFHD)
2x | Mounting Plates
1x | Hip Belt (https://www.moosejaw.com/p/osprey-womens-isoform-cm-hipbelt-23trywsfrmcmhpbltbag/23trywsfrmcmhpbltbag?sku=25482757&gad_source=1&gclsrc=aw.ds)
8x | M5x22mm Button Head Screw (https://www.mcmaster.com/91239A242/)
8x | M5 Nut (https://www.mcmaster.com/91854a102/)
8x | M5 Washer (https://www.mcmaster.com/92334A113/)
8x | M5 Screw Cap (https://www.mcmaster.com/90527A510/)
1x | Drill Press (https://www.amazon.com/WEN-4208T-2-3-Amp-5-Speed-Benchtop/dp/B08ZVT5JKC?hvadid=580530431901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) or Hand Drill (https://www.amazon.com/Cordless-Drill-Driver-Bare-18-0V/dp/B00I3MMYVU?hvadid=693363057790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) (6mm bit) (https://www.amazon.com/COPOUIXR-Cobalt-1-5mm-6-5mm-Material-13-Piece/dp/B0B8WYPBMF?s=industrial)
b) Place the motor mounting plates onto the belt in their desired positions and use a sharpie to mark the places where mounting holes will be drilled into the belt. These should be in the four corners of the plate.


c) Use the added belt markings to drill holes into the belt. These holes should just be through the initial outer layer of the belt and should not puncture into the foam padding component. You should be able to reach into the inner part of the belt and feel the holes without having them go all the way through! (Note: It is advised to use a scrap piece of plastic or other material to prevent the drill from punching past the inner lining of the mounting area. This can be seen in the below image. If not available, just proceed slowly and try to avoid getting into the actual foam padding of the belt).
d) Once all the mounting holes are drilled, place washers onto the M5x22 bolts and insert them into the holes with the heads on the inside of the belt and the ends sticking through the belt as shown below.

e) Place the mounting plates onto the bolts and tightly fasten down M5 nuts using the driver. Once this is done, place the caps onto the bolts. The final product is shown below.

Repeat for other side.

## Mounting the Battery & PCB Casing

Here we will be printing and mounting the Battery and PCB casing to the back of the belt.

1. Printing
These will be long prints. Thus, it is best to print only one or two parts at a time so that if the print fails at any point, less material is wasted. Start by printing the “electronicsBoxBackPlate.SLDPRT” located in the “Part Files for 3D Printing” folder.
2. Mounting
It is best to mount the Battery and PCB case before assembling the device.
a) Gather necessary components.
1x | electronicsBoxBackPlate.SLDPRT
15x | M3 Threaded Inserts (https://www.mcmaster.com/94459A130/)
4x | M3x14 Button Head Screws (https://www.mcmaster.com/92832A566/)
4x | M3 Washers (https://www.mcmaster.com/92334A109/)
1x | Drill Press (https://www.amazon.com/WEN-4208T-2-3-Amp-5-Speed-Benchtop/dp/B08ZVT5JKC?hvadid=580530431901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) or Hand Drill (https://www.amazon.com/Cordless-Drill-Driver-Bare-18-0V/dp/B00I3MMYVU?hvadid=693363057790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) (3mm bit) (https://www.amazon.com/COPOUIXR-Cobalt-1-5mm-6-5mm-Material-13-Piece/dp/B0B8WYPBMF?s=industrial)
1x | Sharpie (https://www.amazon.com/SHARPIE-Black-Markers-Set-High-Quality/dp/B00006IFHD)
1x | Soldering Iron (https://www.uline.com/Product/Detail/H-10799/Anti-Static-Equipment/Weller-Soldering-Station?pricode=WC4573&gadtype=pla&id=H-10799&gad_source=1)
b) Insert the threaded inserts into every hole of the 3D printed backplate. These will allow you to properly fasten the 3D printed part to the belt and to properly secure components (PCB, Strain Relief) to the casing. It should be noted that there are specific orientations that should be followed. The four that secure the casing to the belt should be inserted from the side the PCB would sit (front side, first picture, see red arrows). All other threaded inserts should be placed from the side that would face a person’s back when wearing the hip belt (back side, second picture). This should be an easy convention to follow, as there are shoulders inside the through holes for the threaded inserts corresponding to this pattern. Threaded inserts can be placed by heating a soldering iron, placing its tip into the metal threaded insert, and slowly pressing (and twisting) the insert into the hole until the surface of the threaded insert is flush with the 3D printed material.

c) Take the back plate and align it centrally on the lower middle of the waist belt. Take a sharpie or pen and place the tip into the four centrally placed holes in the backplate (red arrows above) with the goal of marking those hole locations on the belt. These will be the points where we will secure the casing to the belt. Generally, you should have these as low as possible and as evenly leveled as possible.


d) Using a 3 mm diameter bit, drill through these marked locations on the belt. Make sure to puncture all the way through the material and the plastic, out onto the other side.
e) Press four M3 screws with washers on them the through the inside of the belt (Velcro side), as shown.

f) Attach the back plate onto the belt by aligning the four holes with the fasteners. Screw the fasteners into the backplate, securing it to the belt.

## MANUFACTURING THE CARBON FIBER PARTS

Some components of the exo are made from carbon fiber (to retain strength while minimizing weight). If you have access to the necessary tools, this can be done in-house. Otherwise, there are plenty of third-party options online. Importantly, when machining carbon fiber always ensure you are wearing a respirator and eye protection.

All of the machined carbon fiber components can be found in Part Files for Machining > CF Machining.

1. Machining the Parts for Yourself
If you have access to your own CNC, (https://toolstoday.com/stepcraft-3d-600-cnc-system.html) it may be easier to machine these components yourself, as they are fairly simple geometries. Included are tutorial videos for how we machine our carbon fiber components using our in-house CNC. (https://toolstoday.com/stepcraft-3d-600-cnc-system.html) These may be of use for you, and can be found here. (https://youtu.be/3-a7w1pI_XY)

Should you choose to machine these components yourself, ensure that you are protecting yourself from the carbon fiber dust while machining. The dust poses a serious health risk if ingested. Wear a quality respirator and eye protection. Covering as much skin as possible while machining is also recommended.
2. Third-Party Machining
If you do not have the ability to machine these parts yourself, third-party manufacturers, such as Xometry (https://www.xometry.com/capabilities/sheet-cutting/) can do so for you. They can cut contours into carbon fiber plates, which is what you’ll need for the following components, all of which are contained in the CF Machining folder:
- hipAdapterOuter.SLDPRT
- hipAdapterInner.SLDPRT
- motorBracketSpacer.SLDPRT
- motortoStrutSupport.SLDPRT
- thighCuffReinforcement.SLDPRT

There is another carbon fiber component that you’ll need to have manufactured for you (carbonFiberStrut.SLDPRTs). These are one-foot-long pieces of rectangular carbon fiber tubing which serve as the main interface to help transfer motor torque to the wearer. For the carbonFiberStrut.SLDPRT, you’ll need two carbon fiber tubes (https://www.rockwestcomposites.com/25502-group) cut to a length of one foot. Once you have the tubes, three mounting holes need to be drilled. For this, a drill press is best, but a hand drill and a fair amount of diligence can suffice as well. The process for doing so is outlined below.
3. Drilling Mounting Holes into the Carbon Fiber Tubes
a) Gather necessary components.
2x | 1’ Carbon Fiber Tube (https://www.rockwestcomposites.com/25502-group)
1x | Drill Press (https://www.amazon.com/WEN-4208T-2-3-Amp-5-Speed-Benchtop/dp/B08ZVT5JKC?hvadid=580530431901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) or Hand Drill (https://www.amazon.com/Cordless-Drill-Driver-Bare-18-0V/dp/B00I3MMYVU?hvadid=693363057790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) with 5mm Diameter Bit (https://www.amazon.com/COPOUIXR-Cobalt-1-5mm-6-5mm-Material-13-Piece/dp/B0B8WYPBMF?s=industrial)
1x | Silver Sharpie (https://www.amazon.com/Sharpie-39108PP-Metallic-Permanent-Blister/dp/B00009RAX4?hvadid=616991223281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)
1x | holeTemplateForStrut.SLDPRT
b) Slide the holeTemplateForStrut.SLDPRT onto the carbon fiber tube.

c) Using the sharpie, mark the positions where the holes will be drilled. If you’re using a drill press, you only need to mark one side. If you’re using a hand drill, it’s best to mark both sides of the upright and drill both sides independently for the best accuracy.
d) Drill the holes.

e) The carbon fiber tubes are now ready to serve as the uprights for the exoskeleton.

## OBTAINING THE MACHINED ALUMINUM PARTS

We do not manufacture the aluminum abduction/adduction parts in-house due to their complexity. Like the carbon fiber components, it is easy to have a third-party manufacturer do so for you. We have previously used UPTIVE (https://uptivemfg.com/) to manufacture them for us. The part files are provided in the Aluminum Machining folder. The material used for these parts is 7075 Aluminum.

## ASSEMBLING MACHINED COMPONENTS

## 1. Motors onto Belt

Here, we will be using the plastic mounting interfaces, the carbon fiber components, and the externally manufactured aluminum components to attach the motors onto the belt.

a) Gather necessary components.
1x | Belt Assembly
4x | Ball Bearings (https://www.mcmaster.com/7804K143/)
4x | M6 Washers (https://www.mcmaster.com/97725A102/)
2x | 6mm x 25mm Shoulder Screw (https://www.mcmaster.com/90323A466/)
2x | M5 Lock Nut (https://www.mcmaster.com/94205A240/)
8x | M5x14 Button Head Screw (https://www.mcmaster.com/91239A230/)

8x | M5 Nut (https://www.mcmaster.com/91854a102/)
18x | M3x4 Socket Head Screw (https://www.mcmaster.com/91290A109/)
8x | M3x6 Button Head Screw (https://www.mcmaster.com/92832A215/)
2x | AK60v1.1 Motor (https://store.tmotor.com/goods-1201-AK60-6+V11.html)
2x | hipAdapterInner.SLDPRT
2x | hipAdapterOuter.SLDPRT
2x | adAbductionBlockHipSide.SLDPRT
2x | adAbductionBlockLegSide.SLDPRT
b) Remove thermoformed interface from belt.
c) Press the bearings into the hip side abduction/adduction block.
d) Fasten the hip side abduction/adduction block to the thermoformed interface using the M5 x 14 bolts and M5 nuts. You may need to bend the plastic mounting plate to get this to properly fit and, on some occasions, the holes in the mounting plate may need to be slightly expanded to ensure proper fitting (can be done by sanding them).

Side Note: An important thing to consider is where in the mounting plate grid this abduction/adduction block should be placed. We first recommend having the intended user wear the belt with the empty mounting plates (no aluminum blocks) on it. Once this is accomplished, have the top of the belt aligned with the top of their iliac crest and the fronts of the belt’s padding equally aligned with their left and right ASIS while snug on the user. From there find their greater trochanters and then identify the hole patterns in the mount that are in-line with the greater trochanters. It’s possible, depending on the belt used, that this won’t be possible, at which point we would recommend finding a different belt size that will allow for this alignment. Once this hole pattern is identified, fasten the abduction/adduction block to the mounting plates at these locations as described above. Generally, we have used the bottom row of holes for this (as shown in the image) so that the center of the motor is most in-line with the hip joint, but this may need to be adjusted depending on the user. While this generally fitting approach is our

HipAdapterInner.SLDPRT | HipAdapterOuter.SLDPRT | adAbudctionBlockHipSide.SLDPRT adAbudctionBlockLegSide.SLDPRT

recommendation (it seems to be the easiest way to get consistent fitting across users), feel free to explore other potential fitting approaches as you see fit.


e) Once the abduction/adduction block is secure to the mounting plate, refasten thermoformed mounting plates to the belt.
f) Fasten the leg side of the abduction/adduction block to the hip side using the 6mm Diameter x 25mm Length Shoulder Screw, M6 Washers, And an M5 Lock Nut.

g) Fasten both the inner and outer carbon fiber Hip Adapters to the AK60v1.1 motors using a total of nine M3x4 bolts for each. DO NOT OVER TIGHTEN as this may puncture the motor, damaging them and leaving them non-functional. When fastening, ensure that the longer side of the Inner Hip Adapter is facing the back of the belt when the motor is mounted, as shown in the right image below.

Outside

← Back of Belt h) Fasten the motors onto the aluminum block interface using four M3x6 button head screws for each motor (red arrows). We recommend using Loctite (https://www.amazon.com/gp/aw/d/B0CHM5QS3N/?aaxitk=a102eeeb13043268c1484d26cd5125e7&hsa_cr_id=0) during this step to avoid the chance that the screws back out.

## 2. Attaching the Uprights to the Motors

a) Gather necessary components.
2x | motorToStrut.SLDPRT
2x | motorToStrutSupport.SLDPRT
2x | motorBracketSpacer.SLDPRT
2x | boltSupportForStrut.SLDPRT
12x | M3x10 Socket Head Screws (https://www.mcmaster.com/91290A115/)
6x | M5x30 Button Head Screw (https://www.mcmaster.com/90910A582/)
6x | M5 Washers (https://www.mcmaster.com/92334A113/)
6x | M5 Nuts (https://www.mcmaster.com/91854A102/)
2x | carbonFiberStrut.SLDPRT


b) Fasten the motorBracketSpacer, motorToStrutSupport, and motorToStrut to the motor with six M3x10 screws. Once again, do not over tighten as this may puncture and damage the motor. The motorBracketSpacer should be the only part that touches the motor. The motorToStrutSupport should sit inside the motorToStrut. This may require you to press the part in or to do some minor sanding to the spacer to get it to sit properly within the 3D printed spacer. The screws will ensure all the parts are fastened to the center of the motor. [Note: The hip belt is oriented upside down in the following image to provide the clearest view of the assembly].

c) Insert the boltSupportForStrut into the carbon fiber strut and ensure that the holes of the bolt support align with those in the strut.
d) Place the Carbon Fiber Strut onto the motorToStrut, aligning the three M5 holes.
e) Use three M5x30 bolts, M5 washers, and M5 nuts to fasten the strut onto the motorToStrut.

This Completes the Hardware Assembly

## ELECTRICAL COMPONENTS

In this section we will outline the process of making all the electrical components involved with this device. This includes the creation of the CAN communication wiring to facilitate communication between the PCB and the motors, the FSR wiring to facilitate the connection between these external sensors and PCB, and the power cables connecting the battery to the PCB and the PCB to the motors. At the end of this section, an outline for where all the wires should be connected is provided.

## 1. Assembling the CAN Wire

a) Gather necessary components.
1x | Motor-to-Board CAN Wire (https://www.digikey.com/en/products/detail/969M101-28-1TPS-025/CI28E-25-ND/3526257?itemSeq=386416477)
2x | CJT Connectors – Motor End (https://www.lcsc.com/product-detail/Rectangular-Connectors-Housings_CJT-Changjiang-Connectors-A1257H-4P_C339040.html)
4x | CJT Pins – Motor End (https://www.lcsc.com/product-detail/Line-Pressing-Terminals_CJT-Changjiang-Connectors-A1257-TP_C339052.html)
4x | MOLEX Pins – Board End (https://www.digikey.com/en/products/detail/molex/5013340100/1531513)

2x | MOLEX Connectors – Board End (https://www.digikey.com/en/products/detail/molex/5013300200/1531499)
1x | Crimping Tool (https://www.digikey.com/en/products/detail/molex/0638191500/1832244)
1x | Wire Strippers/Cutters (https://www.digikey.com/en/products/detail/tempo-communications/PA1161/461371)
1x | Utility Knife (https://www.amazon.com/24Pack-Utility-Retractable-Compact-Extended/dp/B08H7XQZZ2?s=industrial&sp_csd=d2lkZ2V0TmFtZT1zcF9hdGY)
1x | Heat Shrink (https://www.amazon.com/650pcs-Shrink-Tubing-innhom-Approved/dp/B07WWWPR2X?hvadid=664381657194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)

MOLEX Pin – Board End

b) Cut the Motor-to-Board CAN Wire to the required length. 40 cm should be adequate, but double check whether this is enough for your belt (Make sure they can reach from the motors to the PCB while someone wears the belt). We use and recommend a specific CAN wiring but feel free to swap out with some alternative if you would like.
c) Strip roughly 1 cm of the outer cable on both sides of the wire, revealing the two inner wires. We typically use a box cutter for this step, carefully cutting off the outer shell without cutting into the inner wiring. When you do this, you will typically still get some of the gray inner lining material left around those wires. We recommend peeling this off and trying to cut as much of it off to leave only the wires exposed (see image below).

d) Strip the very ends of these inner wires on both sides to prepare them for crimping. Only a little bit of the inner wire needs to be exposed, so try to strip off as little as possible.


e) Cut two pieces of heat shrink and slide them onto the middle of the cable.
f) Carefully crimp the Molex pins onto one end of the wire (one for the black cable and one for the white cable on the same end of the cable).

g) Crimp the CJT Pins on the other end of the wire.
h) Using the continuity check feature on a multimeter, (https://etekcity.com/products/digital-multimeter-msr-r500) ensure that the connection between each end of the wire is good. To do this, tap each end of the jacks of the multimeter to the opposite end of the same color wire. For example, touch one jack to the CJT pin on the black wire and the other jack to the Molex pin on the black wire. If there is a connection, the multimeter should make a beeping sound. Now, keeping one jack on the black pin, switch one end to the white wire (e.g., move from the black Molex to the white Molex while keeping the other jack on the black CJT pin). No beeping should be coming from the multimeter. If beeping does occur, that means there is a short in the wiring which can create problems and it is likely best if the wire is remade. Repeat this process with the opposite-colored wire (e.g., white).

i) Insert the Molex pins into the Molex connector. Orient the Molex connector such that the tabs side is facing up (see image below). Once the connector is oriented this way, insert the wire connectors such that the white wire is on the right side and the black wire is on the left side, as shown in the image below. The pins should be oriented and slotted into the connector with their metal tab side facing up (red arrow). It may be helpful to have a pair of tweezers to aid in this step.
j) Insert the CJT pins into the CJT connector. Orient the CJT connector such that the tabs side is facing up (see image below). Once the connector is oriented properly, insert the wire connectors such that the black wire is on the rightmost hole and the while wire is in the hole immediately to its left. Ensure the tab on the CJT pin is facing upwards (red arrow) during this step.


k) Slide the heat shrink to the base of the connector on each side and then use the heat gun to shrink the material. It may be helpful to have a pair of tweezers available for this step as well. When completed, the two ends should look like the images below.
l) Repeat the continuity test with the multimeter (as described above) by sticking the tip of each jack onto the exposed metal component for each connector.

Note: If you are having issues with the pins becoming loose and sliding out of the connector, applying some hot glue on the ends of the connectors where the pins are inserted may help alleviate this problem.

## 2. Preparing the FSRs

Here we will make the FSRs (external sensors that will detect heel and toe strike for control estimation). Prior to this, you will need to print four Heel_Puck.SLDPRTs, which are located in FILES FOR USERS/Part Files for 3D Printing.

a) Gather the necessary components.
4x | Force Sensitive Resistors (FSRs) (https://www.tekscan.com/products-solutions/force-sensors/flexiforce-a502-sensor)
1x | 40cm Length Ribbon Cable (https://www.amazon.com/risingsaplings-Ribbon-Rainbow-1-27mm-2-54mm/dp/B097C84H9W)
4x | Pairs of Male Pin Connectors (https://www.amazon.com/2-54mm-Breakaway-Female-Connector-Arduino/dp/B01MQ48T2V)
1x | Heat Shrink (https://www.amazon.com/650pcs-Shrink-Tubing-innhom-Approved/dp/B07WWWPR2X?hvadid=664381657194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) (you will need a smaller and larger size)
1x | Soldering Iron (https://www.uline.com/Product/Detail/H-10799/Anti-Static-Equipment/Weller-Soldering-Station?pricode=WC4573&gadtype=pla&id=H-10799&gad_source=1)
1x | Solder
1x | Heat Gun (https://www.amazon.com/SEEKONE-Heat-Gun-Hot-Air/dp/B078S5QMFG?hvadid=616863312459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)
1x | Tweezers (https://www.amazon.com/kaverme-Anti-Static-Electronics-Laboratory-Jewelry-Making/dp/B0BNNGC3Q2?sp_csd=d2lkZ2V0TmFtZT1zcF9hdGY)
1x | Wire Strippers (https://www.digikey.com/en/products/detail/tempo-communications/PA1161/461371)
2x | Insoles
4x | Heel_Puck.SLDPRT
1x | Gorilla Tape (https://www.amazon.com/Gorilla-Tape-Black-Duct-1-88/dp/B000CSS8UE?th=1) (or something comparable)

Male Pin Connector Pair | heelPuck.SLDPRT
b) Take the ribbon cable, cut it to a length of 40cm. Then split the ribbon cable into separate pairs of two. To split the connectors, we use the edge of a box cutter to get started and from there peeled them apart. You should do this until you have 4 pairs of two wires. From there you should separate both edges of each wire as shown in the images below.


c) Strip all the ends of each wire and then coat each end with solder

d) Slide the smaller diameter heat shrink over each individual wire on one end of the cable. Do not use the heat gun to shrink the material yet.
e) Take the FSR and coat the two exposed metal ends in solder in the same way you coated the ends in the step above.
f) Solder one end of the wire (both components of that end) to the two exposed metal ends for the FSR. Then slide the heat shrink over each soldered end and use the heat gun to shrink them. Be careful not to apply too much heat to the metal connectors of the FSRs as this may cause them to become dislodged, ruining the sensor. Once completed, the FSR should look as below.
g) Slide heat shrink onto the other side of the wires.

h) Solder these wire ends to the short end of the pair of male pin connectors. Prior to soldering it may be helpful to coat the short end of the male connector in solder. Once soldered together, slide the heat shrink over the soldered connections and use the heat gun to shrink them.
i) Slide the larger in diameter heat shrink onto the end just soldered and shrink onto the base of the pin connector and the wires. This will serve as extra protection as well as a handle (see left image below). The entire FSR should look similar to the image below (right)

j) Now we’ll need to secure the FSR to the heelPuck.SLDPRT. To do so, lay the footplate as shown below.
k) Taking your tape, completely wrap the FSR in order to protect it.
l) Tape the FSR to the bottom side of the shoe’s insole about where the ball of your foot rests (as shown in the image below). Be careful not to confuse the orientation when flipping the insole upside down!


m) Place the second FSR at the heel and tape down as well. Ensure that the wires are coming out on the external side of the foot close to where your ankle would be, this will make it easy for the wires to exit the shoe without interfering with movement. It is helpful to guide the wires to the edge and then tape them together along the edge to keep them secure. During this step, make note of which wire is for the toe FSR and which is for the heel FSR. We suggest placing a label or wrapping a piece of tape around one of the wires to help differentiate them.
n) Place the sole back into the shoe and repeat for the other side.

## 3. Wires for Connecting the FSR to the PCB

Here, you will be making the cables that connect the FSRs to the PCB. You will need two of these wires, one for each leg. As a result, the process outlined below will need to be repeated an additional time!

a) Gather necessary components.
1x | FSR-to-Board Connecting Cable (https://www.digikey.com/en/products/detail/tensility-international-corp/30-00491/5819490)
1x | Heat Shrink (https://www.amazon.com/650pcs-Shrink-Tubing-innhom-Approved/dp/B07WWWPR2X?hvadid=664381657194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)
1x | Ribbon Cable Header for Board (https://www.digikey.com/en/products/detail/w%C3%BCrth-elektronik/61200823021/4846918)
2x | 1X5 Female Pin Connectors (https://www.amazon.com/2-54mm-Breakaway-Female-Connector-Arduino/dp/B01MQ48T2V)
1x | 8-Wire Ribbon Cable (https://www.amazon.com/risingsaplings-Ribbon-Rainbow-1-27mm-2-54mm/dp/B097C84H9W)
1x | Soldering Iron (https://www.uline.com/Product/Detail/H-10799/Anti-Static-Equipment/Weller-Soldering-Station?pricode=WC4573&gadtype=pla&id=H-10799&gad_source=1)
1x | Wire Strippers (https://www.digikey.com/en/products/detail/tempo-communications/PA1161/461371)
1x | Solder
1x | Heat Gun (https://www.amazon.com/SEEKONE-Heat-Gun-Hot-Air/dp/B078S5QMFG?hvadid=616863312459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)
Cable | Ribbon Cable Header for Board | 1X5 Female Pin Connector

b) Cut 120 cm of the FSR-to-Board Connecting Cable. This is the black cable with four wires inside, as shown above.
c) Strip roughly 2 cm of the outer cable off both ends of the cable. This will leave the insides exposed which consists of the four wires and inner insulation/sheathing. Remove the inner sheathing/insulation as best you can (we try to twist it off to the side and cut away as much of it as possible with wire cutters/scissors/box cutters).


d) Strip the ends of the four inner wires, on both sides, to prepare for soldering. You only need to strip a small portion off each end.
e) Cut ~4 cm of ribbon cable, ensure it has 8 wires (you can always get a bigger one and remove a few if needed).
f) Separate four of the wires on only one side of the ribbon cable and strip them to prepare for soldering. [Left Image: Four Separated – Brown, Red, Orange, Yellow; Right Image: Four Stripped – Brown, Red, Orange, Yellow]

g) Cut small sections of heat shrink and slide it over those four wires. Then, solder the four ribbon cable wires to the FSR-to-Board Connecting Cable. Once soldered use the heat gun to shrink the heat shrink around the soldered connections. It is important to take note of the order you solder these wires. That is, keep note of what color of the FSR wire is soldered to what color of the ribbon cable. We recommend the following convention (assuming colors align on both the ribbon cable and the FSR wire):
- FSR Black -> Ribbon Cable Brown
- FSR Red -> Ribbon Cable Red
- FSR White -> Ribbon Cable Orange
- FSR Yellow -> Ribbon Calbe Yellow
h) Now we’ll solder the other end of the FSR-to-Board Cable to the 1x5 Female Pin Connector. Order is important here. First, some background information. Below is a diagram indicating the order of the wires in relation to the ribbon cable header that we will eventually place on the ribbon cable we just soldered. The inclusion of this diagram is to make clear the logic behind the order that you will solder wires to the 1X5 Female Pin Connector. Once connected to the PCB, the board will read the wires as follows:
- 1: FSR Toe + | (Ribbon Cable Brown -> FSR Black)
- 2: FSR Heel + | (Ribbon Cable Red -> FSR Red)
- 3: FSR Toe - | (Ribbon Cable Orange -> FSR White)
- 4: FSR Heel - | (Ribbon Cable Yellow -> FSR Yellow)
- 5-8: Unutilized pins for additional sensor (e.g., torque transducer)

Note the orientation of the ribbon cable header in the photo, with the top (solid side) facing upwards and the tab facing towards you. The bottom, with the actual holes is facing down onto the table, we have drawn in the orientation of the holes onto the figure to aid in clarification of the order. The arrow indicates the direction that the ribbon cable will be inserted into the connector. As such, the four leftmost wires of the ribbon cable will be the ones that need to be connected to the FSRs. The other four are available for an additional sensor type (e.g., torque transducer, angle sensor) but for the purposes of this guide we will ignore (but are the reason we have 8 wires for the ribbon cable instead of just isolating to the 4 utilized). [Side Note: If you were to use the remaining four pins for a new sensor type, you would need to change the “Board.h” file in the software as those pins are currently assigned to torque transducers)

When soldering to the 1X5 female pin connector, there will be one extra pin. This is to allow for adequate spacing when connecting the FSRs. This extra pin should be in the middle. You should solder the connections to the female pin connector in the following order:

- Left Most -> Toe + | (FSR Black)
- Second Left Most -> Toe – | (FSR White)
- Middle -> Empty
- Second Right Most -> Heel + | (FSR Red)
- Right Most -> Heel – | (FSR Yellow)
i) Slide larger heat shrink over both ends that you just soldered to enclose the wires. Apply heat to shrink them as a protective covering.

j) Press the 2X4 8-Pin Connector onto the ribbon cable in the orientation shown. This is with the connector holes oriented up and the tab should face towards the main body of the wire. With this orientation, the white (non-connected) side of the ribbon cable should slide into the left side of the connector and the brown (connected) side of the ribbon cable should be on the right side. Once properly oriented, press the two sides of the ribbon cable connector down until firmly pressed together (the two ends should meet). Note that the correct orientation is necessary for proper function of the cable. This should leave you with one cable to connect the PCB to the FSRs in the shoe/insole.


REPEAT THESE STEPS TO MAKE AN IDENTICAL WIRE FOR THE OPPOSITE LEG

## 4. Wiring the Power Switch

a) Gather necessary components.
1x | XT30U Male Connector (https://www.amazon.com/10Pairs-Upgrade-Connector-Female-Battery/dp/B08P5HVMYT)
1x | XT60E1 Male connector (https://www.amazon.com/XT60E-M-Mountable-Connector-Models-Multicopter/dp/B07YJMCDC3?th=1)
1x | Power Switch (https://www.digikey.com/en/products/detail/e-switch/R5ABLKBLKFF0/301976)
NA | Heat Shrink (https://www.amazon.com/650pcs-Shrink-Tubing-innhom-Approved/dp/B07WWWPR2X?hvadid=664381657194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)
2x | 16AWG Wire (https://www.amazon.com/Electrical-Conductor-parallel-silicone-Extension/dp/B07RRPFL3Q) (one red, one black)
2x | 16AWG Nylon Quick Disconnect Female Terminals (https://www.amazon.com/TICONN-Disconnect-Connectors-Electrical-Assortment/dp/B08BZ972B5?cv_ct_cx=ticonn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)
1x | Large Crimping Tool (https://www.amazon.com/Yangoutool-Fishing-Crimping-Crimper-0-1mm-2-2mm/dp/B07PNPZQW8?s=hi)
1x | Wire Strippers/Cutters (https://www.digikey.com/en/products/detail/tempo-communications/PA1161/461371)
1x | Soldering Iron (https://www.uline.com/Product/Detail/H-10799/Anti-Static-Equipment/Weller-Soldering-Station?pricode=WC4573&gadtype=pla&id=H-10799&gad_source=1)
1x | Solder
b) Cut 10 cm of both the positive (red) and negative (black) wires and then strip the ends for soldering.

c) Solder the wires to the XT60E1 Male Connector and apply heat shrink over the connections.


d) Slide another piece of heat shrink over the positive (red) wire (to cover the connection you are about to solder).
e) Solder the positive wire (red) that extends from the XT60E1 Male Connector to the positive terminal of an XT30U Male Connector. Using the heat gun, shrink the heat shrink you slid on to cover the connection.
f) Cut another 10 cm length of black wire and strip both ends.
g) Solder the wire you just prepared to the negative terminal of the XT30U Male Connector. Apply heat shrink to cover the connection. Then cover both connections over this end with a larger heat shrink. Use the heat gun to shrink it down, giving you a firm base to plug/unplug the wire from the board.
h) Crimp the 16AWG Nylon Quick Disconnect Female Terminals onto the two remaining exposed ends of wire. To do this, slide the terminals onto the wiring and use a crimper to squeeze down on the middle portion of the connector.
i) Attach the Power Switch to the two female terminals as shown in the image below. Make sure these two ends are attached to opposite sides of the same horizontal component rather than right next to each other.


## 5. Tapping Holes for the Battery Connector

Here, we’ll tap the holes in the PCB cover’s backplate so that we can fasten the battery connector of the power switch in place.

a) Gather necessary components.
1x | Hip Belt w/ Electronics Box Back Plate attached
1x | M2.5X0.5 Tap (https://www.amazon.com/Aceteel-Metric-Thread-Machine-M2-5x0-5mm/dp/B09SHPBP22)
2x | M2.5X10 Screw (https://www.mcmaster.com/91239A757/)
b) Use the tap to thread the two holes in the battery compartment of the electronics box. You may need a tap wrench (https://www.amazon.com/Groz-9304-T-Handle-Tap-Wrench/dp/B011S64CW6?sp_csd=d2lkZ2V0TmFtZT1zcF9hdGY) for this stage.

c) Screw the battery connector of the power switch into place using two M2.5X10 screws.

## 6. Soldering the Status LED

a) Gather necessary components
1x | RGB LED (https://www.digikey.com/en/products/detail/kingbright/WP154A4SEJ3VBDZGC-CA/7597097)
1x | Ribbon Cable (https://www.amazon.com/risingsaplings-Ribbon-Rainbow-1-27mm-2-54mm/dp/B097C84H9W)
1x | 1x4 Female Pin Connector (https://www.amazon.com/2-54mm-Breakaway-Female-Connector-Arduino/dp/B01MQ48T2V)
1x | Soldering Iron (https://www.uline.com/Product/Detail/H-10799/Anti-Static-Equipment/Weller-Soldering-Station?pricode=WC4573&gadtype=pla&id=H-10799&gad_source=1)
1x | Solder
1x | Heat Gun (https://www.amazon.com/SEEKONE-Heat-Gun-Hot-Air/dp/B078S5QMFG?hvadid=616863312459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)
1x | Wire Strippers/Cutters (https://www.digikey.com/en/products/detail/tempo-communications/PA1161/461371)
NA | Heat Shrink (https://www.amazon.com/650pcs-Shrink-Tubing-innhom-Approved/dp/B07WWWPR2X?hvadid=664381657194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)

b) Isolate about 20cm of four wires of the ribbon cable and separate the ends as shown.
c) Strip the ends of the wires on both sides to prepare for soldering.
d) Cut pieces of heat shrink to size and slide over the wires. After soldering, these will be shrunk to protect the connections.
e) Solder the wires to the 1X4 female pin connector and shrink the heat shrink. Order does not matter in this step.


f) As done before, cut to size and slide heat shrink onto the other ends of the wires and solder to the LED. Order only matters in the sense that the wires are soldered in the same sequence as before (i.e. purple is still next to gray, which is still next to white, which is still next to black).

## 7. Making the Battery-to-Motor Power Cable

a) Gather necessary components
4x | 16 AWG Wire (https://www.amazon.com/Electrical-Conductor-parallel-silicone-Extension/dp/B07RRPFL3Q)
2x | XT30U Male Connector (https://www.amazon.com/10Pairs-Upgrade-Connector-Female-Battery/dp/B08P5HVMYT)
2x | XT30U Female Connector (https://www.amazon.com/10Pairs-Upgrade-Connector-Female-Battery/dp/B08P5HVMYT)
1x | Wire Strippers/Cutters (https://www.digikey.com/en/products/detail/tempo-communications/PA1161/461371)
NA | Heat Shrink (https://www.amazon.com/650pcs-Shrink-Tubing-innhom-Approved/dp/B07WWWPR2X?hvadid=664381657194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)
1x | Heat Gun (https://www.amazon.com/SEEKONE-Heat-Gun-Hot-Air/dp/B078S5QMFG?hvadid=616863312459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)
1x | Soldering Iron (https://www.uline.com/Product/Detail/H-10799/Anti-Static-Equipment/Weller-Soldering-Station?pricode=WC4573&gadtype=pla&id=H-10799&gad_source=1)
1x | Solder
XT30U Male Connector | XT30U Female Connector

b) Cut roughly 40cm of the 16 AWG Wire for the positive and negative connection.
c) Strip both ends to prepare for soldering. Once stripped, it may be helpful to coat each end in a layer of solder to make that process easier.
d) Slide two pieces of heat shrink over both wires on both ends (four total) to protect the solder.
e) Solder the male XT30U to one end and the female XT30U to the other. Cover both ends with a larger piece of heat shrink to help with easy attachment/removal of the wiring.

## 8. Configuring the Motors

a) Gather the necessary components.

1x | R-LINK Module (https://www.mabrobotics.pl/product-page/r-link)
2x | AK60v1.1 Motor (https://store.tmotor.com/goods-1201-AK60-6+V11.html)
1x | Battery-to-Motor Power Cable (from prev. step)
1x | Power Switch Cable (from earlier step)
1x | Battery (https://www.amazon.com/HRB-1800mAh-Helicopter-Airplane-Multicopter/dp/B088QXJNJV/)
1x | USB Cable (https://www.amazon.com/Anker-Charger-Charge-Charging-Samsung/dp/B0BPCZLFS4?c=ts&s=pc&ts_id=464394)
1x | Computer with CubeMarstool_V1.32.exe Installed (located in the same folder as this document)


b) Open the CubeMarstool_V1.32.exe software.
c) Once the software opens, use the switch on the bottom left of the window to switch the language to English, as shown below.
d) Connect the R-LINK Module to the computer with a USB cable.

Power Switch Cable e) Connect the 3-pin and 4-pin cables from the R-LINK to the motor, as shown in the image. The tabs on the connectors should face outwards.

f) Plug the battery into the motor via the battery-to-motor cable and the battery-to-switch connectors. Power on the motor.
g) In the CubeMarsTool window, press the refresh button. The software should auto select the correct COM port. If it does not, you can use the dropdown to select manually.
h) Click “Connect.” A green bar like the one below should flash briefly at the bottom of the screen as confirmation.
i) On the right side of the screen, switch to MIT control. Click Debug.
j) Hold the motor such that it can spin freely. Go down to the bottom of the window and type in the command line “calibrate.” For this to occur, you will need to remove the upright configuration from the motor. It may be easier to do this step prior to placing the motors onto the belt. Once the motor is done calibrating, you will be presented with commands that you can use, as below.


k) Type “setup” in the command line. You will be presented with text similar to that shown below. Notice specifically the “prefix,” “parameter,” and “current value” sections [red boxes]
l) Configure the motor according to the settings in the image below. In order to do so, type the “prefix” for the setting (shown above and below, directly under the “Configuration Options” text), then separated by a space type the desired value. (Example: set_can_id 65). The one option you will need to change, depending on joint and leg you are targeting, is the CAN ID. Use the following convention:
- Left Hip: 65

- Right Hip: 33
- Left Knee: 66
- Right Knee: 34
- Left Ankle: 68
- Right Ankle: 36

So, for the hip device, you would want to set the CAN ID for the motor on the left side to 65 (as shown in the image) and to 33 for the motor on the right side! It may be helpful to place labels on the motors indicating which side and joint they are for during this stage in order to avoid confusion down the road.

m) Once the remaining “current values” are the same as ours, type “exit” in the command line.
n) Click “Disconnect” and you are finished configuring the motor. Repeat for the other motors.

## 9. Making the Connections

a) Gather the hip belt and all the wires you’ve made so far, as well as the electronicsBoxStrainRelief[Left/Right].SLDPRT.
b) Fasten the PCB to the electronics box back plate using the 3 mounting holes which have threaded inserts in them.

c) Connect power and CAN cables to both motors. The power cable goes in the power slot and the CAN communication goes into the connection with 4 pins. Labeled “CAN In & Out” on the side of the motor). Once connected, it may be helpful to add some strain relief in the form of a zip tie. This can be accomplished by zip tying the two cables onto the abduction/adduction block (right image below).
d) Connect all wires as shown in the image below. The ordering convention that we use, should you want to do multi-joint applications, is that the proximal joint goes in the top slots and the more distal joint goes in the bottom slot. In this case, the power cables go in


the first power connector and the CAN communication wiring goes into the top ports on each side. Finally, make sure to plug in the battery-to-switch connector and the ribbon cables.

e) Fasten the strain reliefs to the board. Note that there is a left and right side; the slots in each strain relief correspond to the placement of the ribbon cable on each side of the board.

Left Hip
Power Cable

Left Hip
CAN Cable

Left Hip
Ribbon Cable

Teensy 4.1
With SD Card

Arduino Nano
BLE33 V1

Right Hip
Power Cable

Right Hip
Ribbon Cable

Right Hip
CAN Cable

Battery to Board
Connector

f) Connect the status LED to the board and slide into its respective hole in the panel containing the power switch.

g) Power the board on to ensure that the LED functions. If it does not, reverse the orientation of its connector and try again.
h) During this stage, you should also take the time to connect the heel and toe FSRs on both sides. If you aren’t sure which wires correspond to the heel or toe, you can test to figure it

Teensy

Nano out by pressing each sensor and reading the data. Generally, the shorter wire should belong to the heel since it is oriented away from the connection on the actual insole itself. It may be helpful to make a marking on the FSR connection cable indicating which side is the toe for future usage (one convention we have used is shading the Toe+ connection on the female header a white color to make it stand out).

## ASSEMBLING THE PCB COVER

Now that the wiring is complete, we can assemble the rest of the PCB casing. You’ll need to gather all of the components you’ve printed for the PCB cover.

a) Gather necessary components.
1x | Hip Belt (as left off in the previous section)
1x | electronicsBoxBatteryCover.SLDPRT
1x | electronicsBoxControlPanel.SLDPRT
1x | electronicsBoxStrainReliefLeft.SLDPRT
1x | electronicsBoxStrainReliefRight.SLDPRT
1x | electronicsBoxBody.SLDPRT
4x | M3 Threaded Inserts (https://www.mcmaster.com/94459A130/)
1x | Soldering Iron (https://www.uline.com/Product/Detail/H-10799/Anti-Static-Equipment/Weller-Soldering-Station?pricode=WC4573&gadtype=pla&id=H-10799&gad_source=1)
6x | M3X10 Screws (https://www.mcmaster.com/91290A115/)
a) Use the soldering iron to place M3 threaded inserts into each of the four mounting holes.
b) Press the switch and LED into the electronicsBoxControlPanel.SLDPRT. (Note: The below images do not have the LED, but you should have it during this stage).


c) Place the battery into the top compartment of the electronics box backplate as shown below with the battery’s power wire protruding through the slot.
d) Fasten the electronicsBoxBatteryCover.SLDPRT over the battery with an M3X10 screw.

e) Fasten the electronicsBoxControlPanel.SLDPRT with the switch in it to the electronicsBoxBody.SLDPRT with four M3X10 screws.
f) Connect the switch to both the board and the battery and fasten the electronicsBoxBody.SLDPRT with the switch in it to the backplate.


## PADDING FOR ADDITIONAL COMFORT

You may want to make a pad that fits onto the inner side of the hip belt for additional comfort (example below). These were made by making a pocket with two different fabrics. One softer and breathable for the side facing the user, and a tougher side to which Velcro is sewn. Foam was placed into the pocket (the same foam used for making the insoles) and the pocket was sewn shut. Alternatively, you could take a piece of foam and attach Velcro and that should work somewhat well too.

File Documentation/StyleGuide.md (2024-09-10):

# OpenExo C++ Style Guide 
Based on https://github.com/isocpp/CppCoreGuidelines
and https://www.python.org/dev/peps/pep-0008/

## General 
- Avoid extra whitespace
- 4 space tab
- DON'T place two statements on the same line
- DON'T use void as an argument type
- If globals exist still pass them by reference
- Place curly bracket { on the next line when opening a multiline section.
- Always run interactions through items from proximal joint to distal, and left before right.

## Commenting
- Use docstring (/*  */) for namespaces, types, methods, functions, and constants use explination before definition.
- State intent in comments, not just a restatement of what is readible in the code.
- Comment code as you go so you know what you were trying to do.

## Naming
- Wrap globals in a namespace, e.g. board::can_rx.  Pick a logical namespace name, can be after the header file it is found, but you may want multiple namespaces within one header.
- ALL_CAPS for macro names only, this avoid thinking something is a macro when it is subject to type rules.

### Functions
- Function names should be lowercase, with words separated by underscores as necessary to improve readability.

### Classes
- Class names should normally use the CapWords convention.
- Methods should use function naming convention.
- Private/protected members should use a leading underscores
- Abstract classes should use a leading underscore, ex. _AbstractClass 
- There should not be any public member variables,  members should be accessed with get and set functions.

### Types
- Type variable names should use CapWord Convention

### Variables
- Never use the characters 'l' (lowercase letter el), 'O' (uppercase letter oh), or 'I' (uppercase letter eye) as single character variable names.
- Variable names should follow function naming convention
- DON'T include type in the name, e.g. int_use_this

### Enum
- use enum class rather than typedef.

### Namespace
- Namespaces should normally use the CapWords convention.

### Misc
- Angles should be in radians if not specified.

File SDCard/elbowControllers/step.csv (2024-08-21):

5 | header Size, the first N rows will be ignored, except for this first cells in the first two rows
9 | parameter number, the number of parameters to read per line
 | Parameter list for the Sine controller
 | Parameter order:
Amplitdue | Duration | Repetitions | Spacing | PID Flag | P Gain | I Gain | D Gain | Alpha
1 | 2 | 2 | 2 | 0 | 12 | 0 | 50 | 1

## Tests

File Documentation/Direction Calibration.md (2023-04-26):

# Purposes
After you have built an exo, one of the first things to check is motor directions and the signs (positive/negative) torque sensors and angle sensors return. Having the correct motor directions is important because it allows the exo controller designers, when designing the control algorithms, to focus on the control itself, knowing that, if calibrated properly before use, the exo assistance will always be in the designed directions. The same principle goes to the torque sensors and angle sensors. Since PID control is implemented in many of our exo controllers, it is crucial to make sure that the directions match. This article will elaborate how to conduct the direction calibration. On each exo, this calibration process only needs to be done **once**, its results will need to be **manually** saved on the microSD card and will be loaded **automatically** every time the exo starts up.

## Motor directions
When designing a controller, the values returned from the "calc_motor_cmd()" function determines the motor torque command (feedforward). To ease the controller design process, we propose that controller designers follow the following direction definitions for torque commands:
- At both ankle joints: Positive for Dorsiflexion, and negative for Plantarflexion
- At both knee joints: Positive for Extension, and negative for Flexion
- At both hip joints: Positve for Flexion, and negative for Extension
- At both shoulder joints: Positive for Flexion, and negative for Extension
- At both elbow joints: Positive for Flexion, and negative for Extension

In summary, this follows the Right-hand rule.

## Torque sensor signs (positive/negative)
Following the motor direction definitions, we need to verify that, when the motor supplies a positive torque command, the torque sensors, when zeroed properly, also returns a positive reading when the motor shaft is not spinning.

# How to calibrate
1. To calibrate, set Direction Calibration Manager as the default controller for the current exo. Connect the Teensy to a computer through USB, open up Arduino Serial monitor. Connect the exo (Arduino Nano) with the phone app through Bluetooth, power on the exo and start a new session. The Direction Calibration Manager will send a positive torque command (3.5 Nm by default) to each motor.
2. Feel each torque through, for example, the foot plates on an ankle exo. If the torque applied on, for example, the left foot plate, is not causing it to rotate in the positive direction (see above for the specific directions), flip the motor direction for the left side. Flipping the motor direction is done by modifying the "config.ini" on the microSD card.
3. After modifying all motor directions (if needed), start over again, and this time focus on the torque sensor readings shown on the Arduino Serial Monitor. Feel the motor torque through, for example, a foot plate on an ankle exo, manually move the foot plate back to its neutral position, 0 degree for example. If the corresponding torque sensor does not return a postive value, flip the torque sensor direction by modifying the "config.ini" on the microSD card. Go through all torque sensors (if needed).

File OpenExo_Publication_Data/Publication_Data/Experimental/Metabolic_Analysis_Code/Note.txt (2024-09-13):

You should only have to run Metabolic_analysis.m but I included all for completeness

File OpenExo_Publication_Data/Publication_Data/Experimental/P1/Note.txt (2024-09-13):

"baseline start" = start of quiet standing baseline metabolic measurement
"baseline end" = end of quiet standing baseline metabolic measurement

"exo1_start" = start of timed walking, once treadmill was up to speed
"exo1_end" = end of timed walking, once eight minutes had elapsed.

"#Min" = is the number of minutes since the start data marker, rounded to the nearest available data point
[Do to inconsitent sampling of the device there was not always a data point availabe at the #Min exactly]

In Shod_Metabolic, you will notice that it says "exo1_start" and "exo1_end". 
While labeled this way, the participant did NOT walk with the exo in this condition.
These labels were maintained despite being misrepresntative to make using the processing code as easy as possible to run without having to change it.
[With hindsight it would have been better to use generic terminology like "start" and "end" in the processing code]

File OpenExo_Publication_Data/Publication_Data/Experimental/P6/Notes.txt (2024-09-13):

EMG previously processed as described in Colley et al. (2024). Please reference that for details. 
File contains EMG from other tasks.
MVIC values hard coded in 

Data can be found here: https://drive.google.com/drive/folders/1fx4A6N2uzEDUWUE-o8SEh4-bvtEjuoau?usp=drive_link

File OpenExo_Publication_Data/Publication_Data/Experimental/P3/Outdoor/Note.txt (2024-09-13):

"Outdoor_Results" contains the recorded values (and subsequently calculated values) from the test.

While no metabolic results were presented in the text, we did collect metabolic data which is included here.
These data were not presented in the paper as they were not collected in a way that facilitated a comparison between conditions. 
This includes unstandardized speeds/durations of the task and the fact that no data was recorded for a few minutes after the collection 
to account for the metabolic delay. Data and a modified code to assess it are included for full transparency.

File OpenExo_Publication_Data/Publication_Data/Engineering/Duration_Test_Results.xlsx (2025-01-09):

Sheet: Hip
Minute | Voltage | Left Temp | Right Temp | Average Temp [F] | Average Temp [C]
0 | 25 | 73.8 | 73.7 | 73.8 | 23.2
1 | 24.7 | 77.3 | 77.3 | 77.3 | 25.2
2 | 24.6 | 83.1 | 83.2 | 83.2 | 28.4
3 | 24.5 | 87 | 86.6 | 86.8 | 30.4
4 | 24.4 | 92.6 | 92 | 92.3 | 33.5
5 | 24.3 | 96.9 | 96.1 | 96.5 | 35.8
6 | 24.1 | 101.4 | 101.1 | 101.2 | 38.5
7 | 24.2 | 106.5 | 105.2 | 105.8 | 41.0
8 | 23.9 | 111.2 | 109.3 | 110.2 | 43.5
9 | 23.8 | 115.1 | 113.8 | 114.4 | 45.8
10 | 23.7 | 119.4 | 118.2 | 118.8 | 48.2
11 | 23.7 | 122.9 | 120.6 | 121.8 | 49.9
12 | 23.5 | 126.6 | 123.9 | 125.2 | 51.8
13 | 23.4 | 130.2 | 127.8 | 129.0 | 53.9
14 | 23.5 | 133.5 | 130.3 | 131.9 | 55.5
15 | 23.3 | 136.5 | 132.4 | 134.4 | 56.9
16 | 23.4 | 138.7 | 136.2 | 137.4 | 58.6
17 | 23.2 | 142.2 | 138.6 | 140.4 | 60.2
18 | 23.2 | 143.9 | 140.4 | 142.2 | 61.2
19 | 23.2 | 146.6 | 142.3 | 144.4 | 62.5
20 | 23.1 | 148.2 | 144.8 | 146.5 | 63.6
21 | 23 | 150.8 | 146.6 | 148.7 | 64.8
22 | 23 | 152.8 | 148.1 | 150.4 | 65.8
23 | 22.9 | 154.4 | 149.7 | 152.1 | 66.7
24 | 22.8 | 156.3 | 151.5 | 153.9 | 67.7
25 | 22.7 | 158.3 | 153.1 | 155.7 | 68.7
26 | 22.7 | 159.8 | 154.8 | 157.3 | 69.6
27 | 22.7 | 161.3 | 156 | 158.7 | 70.4
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

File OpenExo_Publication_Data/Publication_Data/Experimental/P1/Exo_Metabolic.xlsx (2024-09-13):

P1 | Test date | 10/31/2023 | Barometric Pressure (mmHg) | 599 | t | Rf | VT | VE | IV | VO2 | VCO2 | RQ | O2exp | CO2exp | VE/VO2 | VE/VCO2 | VO2/Kg | METS | FeO2 | FeCO2 | FetO2 | FetCO2 | FiO2 | FiCO2 | PeO2 | PeCO2 | PetO2 | PetCO2 | Phase | Marker | Amb. Temp. | RH Amb | Device Temp. | Analyz. Press. | PB | EEkc | EEh | EEm | EEtot | EEkg | PRO | FAT | CHO | PRO% | FAT% | CHO% | npRQ | Long | Lat | GPS Altitude | Barom_Altitude | GPS Speed | GPS Dist. | Ti | Te
Last Name | Test Time | 4:02 PM | Ambient Temperature (°C) | 20 | s | 1/min | L(btps) | L/min | mL | mL/min | mL/min | --- | mL | mL | --- | --- | mL/min/Kg | --- | % | % | % | % | % | % | mmHg | mmHg | mmHg | mmHg | --- | --- | °C | % | °C | mmHg | mmHg | kcal/day | kcal/h | kcal/min | kcal | kcal/Kg/day | kcal/day | kcal/day | kcal/day | % | % | % | --- | ° ' " | ° ' " | m | m | km/h | m | s | s
First Name | Test Duration | 0:15:52 | Ambient Relative Humidity (%) | 32
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

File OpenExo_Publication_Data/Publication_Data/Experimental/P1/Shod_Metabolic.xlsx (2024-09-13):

P1 | Test date | 10/31/2023 | Barometric Pressure (mmHg) | 599 | t | Rf | VT | VE | IV | VO2 | VCO2 | RQ | O2exp | CO2exp | VE/VO2 | VE/VCO2 | VO2/Kg | METS | FeO2 | FeCO2 | FetO2 | FetCO2 | FiO2 | FiCO2 | PeO2 | PeCO2 | PetO2 | PetCO2 | Phase | Marker | Amb. Temp. | RH Amb | Device Temp. | Analyz. Press. | PB | EEkc | EEh | EEm | EEtot | EEkg | PRO | FAT | CHO | PRO% | FAT% | CHO% | npRQ | Long | Lat | GPS Altitude | Barom_Altitude | GPS Speed | GPS Dist. | Ti | Te
Last Name | Test Time | 3:30 PM | Ambient Temperature (°C) | 20 | s | 1/min | L(btps) | L/min | mL | mL/min | mL/min | --- | mL | mL | --- | --- | mL/min/Kg | --- | % | % | % | % | % | % | mmHg | mmHg | mmHg | mmHg | --- | --- | °C | % | °C | mmHg | mmHg | kcal/day | kcal/h | kcal/min | kcal | kcal/Kg/day | kcal/day | kcal/day | kcal/day | % | % | % | --- | ° ' " | ° ' " | m | m | km/h | m | s | s
First Name | Test Duration | 0:13:50 | Ambient Relative Humidity (%) | 32
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

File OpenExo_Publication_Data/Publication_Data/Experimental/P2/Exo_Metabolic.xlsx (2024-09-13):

P2 | Test date | 11/21/2023 | Barometric Pressure (mmHg) | 604 | t | Rf | VT | VE | IV | VO2 | VCO2 | RQ | O2exp | CO2exp | VE/VO2 | VE/VCO2 | VO2/Kg | METS | FeO2 | FeCO2 | FetO2 | FetCO2 | FiO2 | FiCO2 | PeO2 | PeCO2 | PetO2 | PetCO2 | Phase | Marker | Amb. Temp. | RH Amb | Device Temp. | Analyz. Press. | PB | EEkc | EEh | EEm | EEtot | EEkg | PRO | FAT | CHO | PRO% | FAT% | CHO% | npRQ | Long | Lat | GPS Altitude | Barom_Altitude | GPS Speed | GPS Dist. | Ti | Te
Last Name | Test Time | 10:40 AM | Ambient Temperature (°C) | 21 | s | 1/min | L(btps) | L/min | mL | mL/min | mL/min | --- | mL | mL | --- | --- | mL/min/Kg | --- | % | % | % | % | % | % | mmHg | mmHg | mmHg | mmHg | --- | --- | °C | % | °C | mmHg | mmHg | kcal/day | kcal/h | kcal/min | kcal | kcal/Kg/day | kcal/day | kcal/day | kcal/day | % | % | % | --- | ° ' " | ° ' " | m | m | km/h | m | s | s
First Name | Test Duration | 0:15:06 | Ambient Relative Humidity (%) | 23
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

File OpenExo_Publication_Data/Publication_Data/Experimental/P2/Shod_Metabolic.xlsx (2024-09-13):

P2 | Test date | 11/21/2023 | Barometric Pressure (mmHg) | 604 | t | Rf | VT | VE | IV | VO2 | VCO2 | RQ | O2exp | CO2exp | VE/VO2 | VE/VCO2 | VO2/Kg | METS | FeO2 | FeCO2 | FetO2 | FetCO2 | FiO2 | FiCO2 | PeO2 | PeCO2 | PetO2 | PetCO2 | Phase | Marker | Amb. Temp. | RH Amb | Device Temp. | Analyz. Press. | PB | EEkc | EEh | EEm | EEtot | EEkg | PRO | FAT | CHO | PRO% | FAT% | CHO% | npRQ | Long | Lat | GPS Altitude | Barom_Altitude | GPS Speed | GPS Dist. | Ti | Te
Last Name | Test Time | 10:04 AM | Ambient Temperature (°C) | 20 | s | 1/min | L(btps) | L/min | mL | mL/min | mL/min | --- | mL | mL | --- | --- | mL/min/Kg | --- | % | % | % | % | % | % | mmHg | mmHg | mmHg | mmHg | --- | --- | °C | % | °C | mmHg | mmHg | kcal/day | kcal/h | kcal/min | kcal | kcal/Kg/day | kcal/day | kcal/day | kcal/day | % | % | % | --- | ° ' " | ° ' " | m | m | km/h | m | s | s
First Name | Test Duration | 0:14:06 | Ambient Relative Humidity (%) | 23
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

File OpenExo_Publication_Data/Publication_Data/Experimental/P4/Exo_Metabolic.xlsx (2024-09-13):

P4 | Test date | 11/1/2023 | Barometric Pressure (mmHg) | 598 | t | Rf | VT | VE | IV | VO2 | VCO2 | RQ | O2exp | CO2exp | VE/VO2 | VE/VCO2 | VO2/Kg | METS | FeO2 | FeCO2 | FetO2 | FetCO2 | FiO2 | FiCO2 | PeO2 | PeCO2 | PetO2 | PetCO2 | Phase | Marker | Amb. Temp. | RH Amb | Device Temp. | Analyz. Press. | PB | EEkc | EEh | EEm | EEtot | EEkg | PRO | FAT | CHO | PRO% | FAT% | CHO% | npRQ | Long | Lat | GPS Altitude | Barom_Altitude | GPS Speed | GPS Dist. | Ti | Te
Last Name | Test Time | 1:24 PM | Ambient Temperature (°C) | 19 | s | 1/min | L(btps) | L/min | mL | mL/min | mL/min | --- | mL | mL | --- | --- | mL/min/Kg | --- | % | % | % | % | % | % | mmHg | mmHg | mmHg | mmHg | --- | --- | °C | % | °C | mmHg | mmHg | kcal/day | kcal/h | kcal/min | kcal | kcal/Kg/day | kcal/day | kcal/day | kcal/day | % | % | % | --- | ° ' " | ° ' " | m | m | km/h | m | s | s
First Name | Test Duration | 0:16:18 | Ambient Relative Humidity (%) | 33
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

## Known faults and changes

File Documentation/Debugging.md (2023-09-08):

This document has some tips to help you through the software debugging process. Once you 
have made sure that you have a software issue (by testing the system with different hardware),
you should begin the software debugging proccess.  

# Overview
The debugging process can be divided into several parts. 
1. Isolation
2. Correction
3. Validation

# Isolation
The isolation step is where you determine what portion of code is causing your issue. For Arduino
we use Serial.print() in various code sections to determine where the error is. 

# Correction
Once you isolate the section of code causing your issue you must fix it! Ideally this can be done
by changing a line or two, but you may have to implement some new functionality. Be sure to develop
in a way that doesn't impact other users. 

# Validation
After you've made your changes, you must validate them. Test the code thoroughly on all supported
boards and/or systems before merging with main. Make sure your changes dont slow down the codebase
by profiling the runtime.

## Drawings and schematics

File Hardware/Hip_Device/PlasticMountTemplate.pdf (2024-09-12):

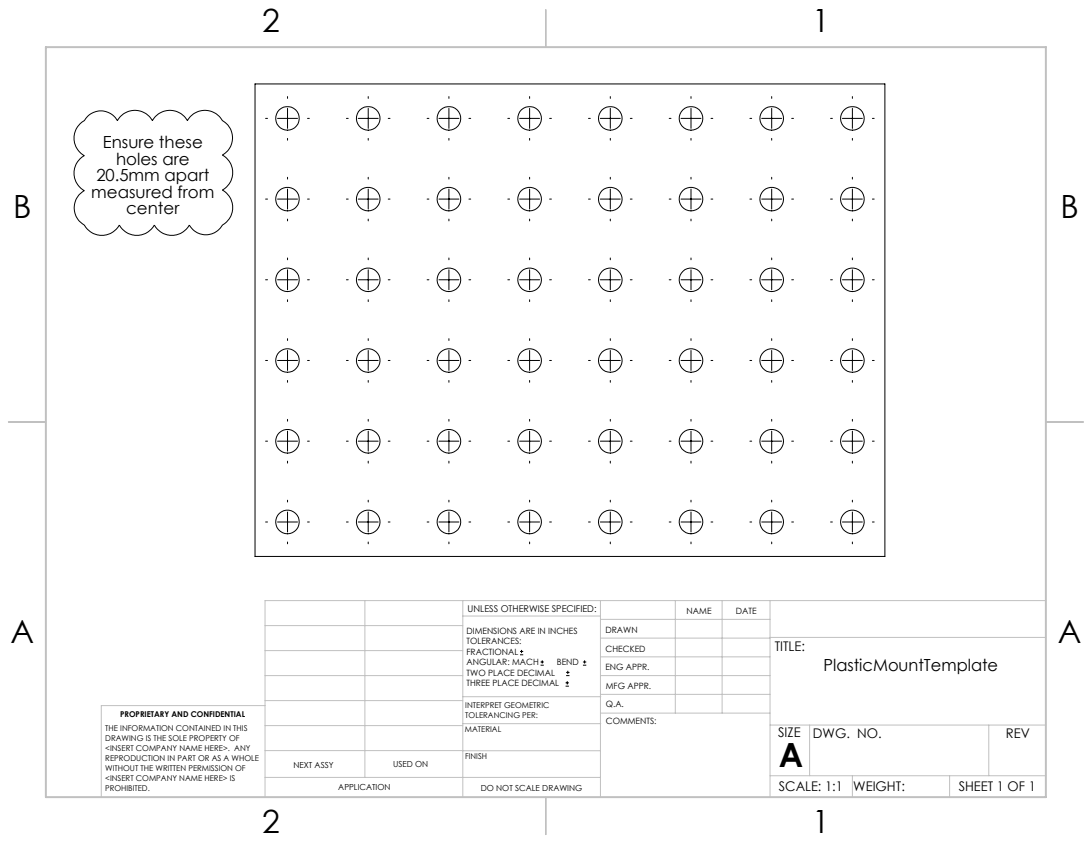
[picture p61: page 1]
Ensure these holes are 20.5mm apart measured from

UNLESS OTHERWISE SPECIFIED: | | NAME | DATE
DIMENSIONS ARE IN INCHES TOLERANCES: FRACTIONAL ANGULAR: MACH BEND TWO PLACE DECIMAL THREE PLACE DECIMAL | DRAWN

CHECKED | | | TITLE: PlasticMountTemplate

ENG APPR.
MFG APPR.

INTERPRET GEOMETRIC TOLERANCING PER: | Q.A.
MATERIAL | | SIZE A | DWG. NO. | REV

PROPRIETARY AND CONFIDENTIAL
THE INFORMATION CONTAINED IN THIS
DRAWING IS THE SOLE PROPERTY OF
<INSERT COMPANY NAME HERE>. ANY
REPRODUCTION IN PART OR AS A WHOLE
WITHOUT THE WRITTEN PERMISSION OF
<INSERT COMPANY NAME HERE> IS
PROHIBITED.

NEXT ASSY | USED ON | FINISH

APPLICATION | DO NOT SCALE DRAWING | | SCALE: 1:1 | WEIGHT: | SHEET 1 OF 1

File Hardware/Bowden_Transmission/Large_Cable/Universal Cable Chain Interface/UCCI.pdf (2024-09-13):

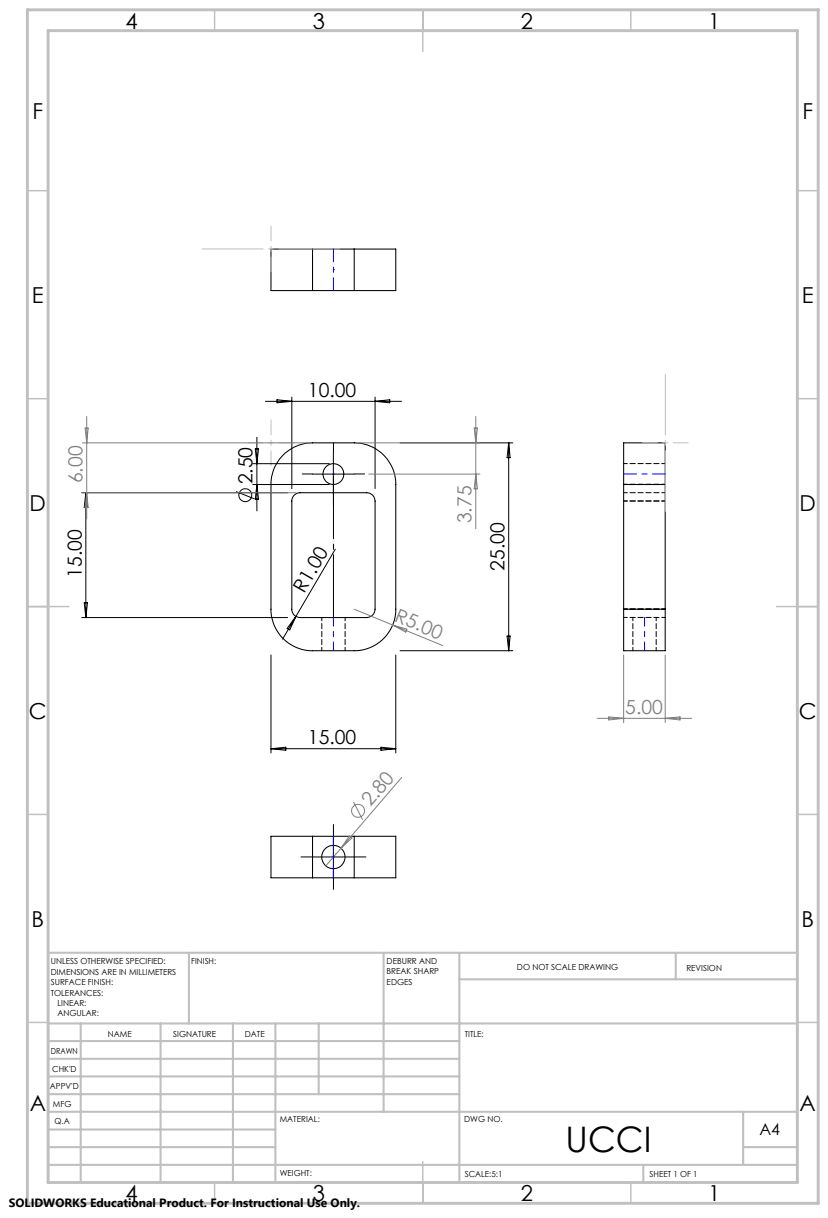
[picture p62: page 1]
FINISH:; DEBURR AND; BREAK SHARP; DO NOT SCALE DRAWING; REVISION; SCALE:5:1; SHEET 1 OF 1

UNLESS OTHERWISE SPECIFIED:
DIMENSIONS ARE IN MILLIMETERS
SURFACE FINISH:
TOLERANCES:
LINEAR:
ANGULAR:

NAME | SIGNATURE | DATE | | | | TITLE:

DRAWN
CHK'D
APPV'D
MFG
Q.A | | | | MATERIAL: | DWG NO. UCCI | A4

SOLIDWORKS Educational Product. For Instructional Use Only.

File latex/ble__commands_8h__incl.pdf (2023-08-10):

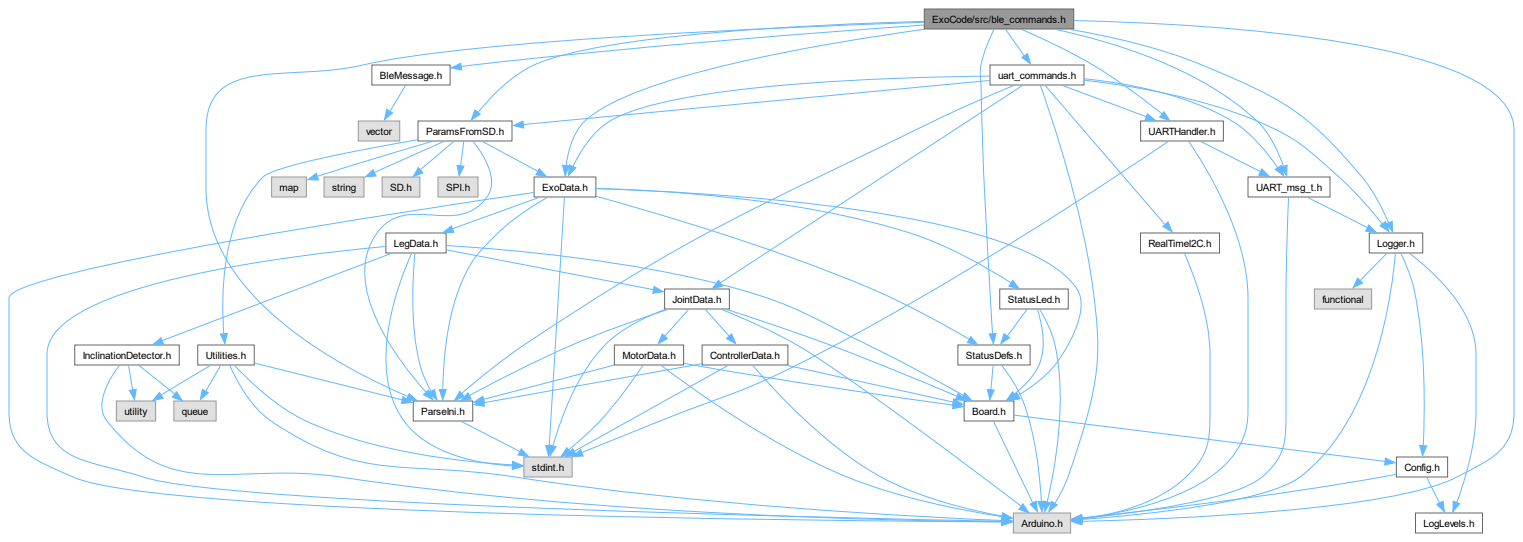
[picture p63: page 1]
ExoCode/src/ble_commands.h; Arduino.h; ExoData.h; ParseIni.h; StatusDefs.h; BleMessage.h; ParamsFromSD.h; UARTHandler.h; UART_msg_t.h; Logger.h; uart_commands.h; LegData.h; stdint.h; Board.h; JointData.h; StatusLed.h; InclinationDetector.h; MotorData.h; ControllerData.h; Config.h; LogLevels.h; utility; queue; vector; Utilities.h; map; string; SPI.h; functional; RealTimeI2C.h

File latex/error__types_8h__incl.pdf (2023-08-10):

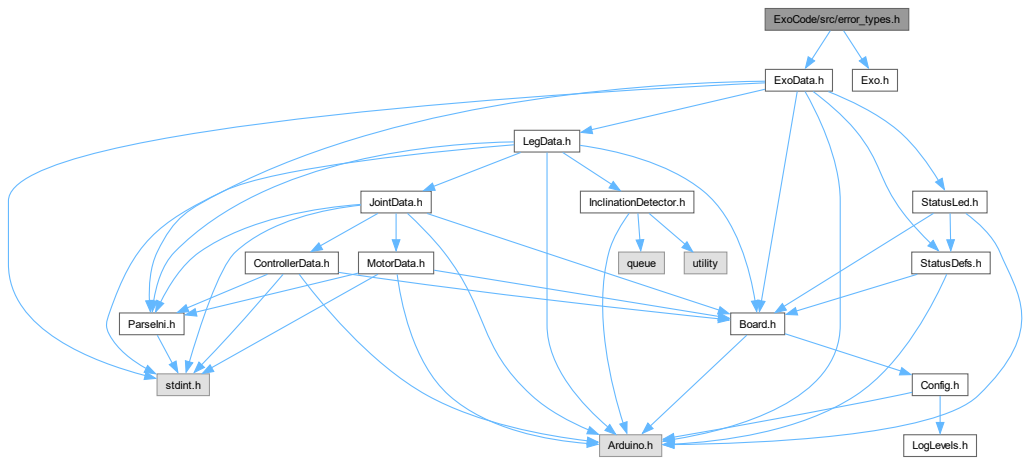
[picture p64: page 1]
ExoCode/src/error_types.h; ExoData.h; Exo.h; Arduino.h; LegData.h; ParseIni.h; stdint.h; Board.h; StatusLed.h; StatusDefs.h; JointData.h; InclinationDetector.h; ControllerData.h; MotorData.h; Config.h; LogLevels.h; queue; utility

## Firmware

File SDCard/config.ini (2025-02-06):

;Board information
;ALL FIELDS SHOULD BE LESS THAN 25 CHAR
[Board]
	name = AK_Board
	version = 0.5.1

[Exo]
	name = bilateralHip
    
[Battery]
    	;Describes the type of battery used, values: smart(inspired energy), dumb (simple lipo)
	name = dumb

[test]
	;Sides - left, right, bilateral	
	sides = bilateral

	;Joints used and their motor name, 0 = not useed, AK60, AK60v1.1, AK70, are AK80 the different CAN motors.
    	;Values 0(not used), AK60, AK60v1.1, AK70, AK80, MaxonMotor
	hip = 0
	knee = 0
	ankle = 0
	elbow = 0
    
    	;Joint gear ratio = velocity of driving member (motor)/velocity of the driven member (output shaft), assumes constant gearing ratio. If the motor spins 6 revolutions to 1 revolution of the output this value would be 6.
    	;This is for transmission gearing after the motor output shaft. If the Motor has a built in gearing that should be part of the motor class (see motor.h/.cpp)
    	;Values 1, 2, 3, 4.5
	hipGearRatio = 1
	kneeGearRatio = 1
	ankleGearRatio = 4.5
	elbowGearRatio = 4.5

	;Default controller for the joint
	;Hip Controllers: zeroTorque, franksCollinsHip, constantTorque, chirp, step, phmc
	;Knee Controllers: zeroTorque, constantTorque, chirp, step
	;Ankle Controllers: zeroTorque, PJMC, zhangCollins, constantTorque, TREC, calibrManager, chirp, step, SPV2 
	;Elbow Controllers: zeroTorque, elbowMinMax, calibrManager, chirp, step
	hipDefaultController = 0
	kneeDefaultController = 0
	ankleDefaultController = 0
	elbowDefaultController = 0
    
    	;Do you want to use a torque sensor for these joints, 0 = no, yes = yes
	hipUseTorqueSensor = 0
	kneeUseTorqueSensor = 0
	ankleUseTorqueSensor = 0
	elbowUseTorqueSensor = 0

	;Flip direction for the motor cmd, 0 neither, left, right, both
	hipFlipMotorDir = 0
	kneeFlipMotorDir = 0
	ankleFlipMotorDir = 0
	elbowFlipMotorDir = 0

	;Flip direction for the torque sensor readings, 0 neither, left, right, both
	hipFlipTorqueDir = 0
	kneeFlipTorqueDir = 0
	ankleFlipTorqueDir = 0
	elbowFlipTorqueDir = 0

	;Flip direction for the angle sensor readings, 0 neither, left, right, both
	hipFlipAngleDir = 0
	kneeFlipAngleDir = 0
	ankleFlipAngleDir = 0
	elbowFlipAngleDir = 0

	;Exoskeleton joint range of motion in degrees
	leftHipRoM = 0
	rightHipRoM = 0
	leftKneeRoM = 0
	rightKneeRoM = 0
	leftAnkleRoM = 0
	rightAnkleRoM = 0
	leftElbowRoM = 0
	rightElbowRoM = 0
	
	;Torque sensor calibration results, a value of "255" leads to the calibration value being utilizied
	leftHipTorqueOffset = 255
	rightHipTorqueOffset = 255
	leftKneeTorqueOffset = 255
	rightKneeTorqueOffset = 255
	leftAnkleTorqueOffset = 255
	rightAnkleTorqueOffset = 255
	leftElbowTorqueOffset = 255
	rightElbowTorqueOffset = 255

[bilateralHipAnkle]
	;Sides - left, right, bilateral	
	sides = bilateral

	;Joints used and their motor name, 0 = not useed, AK60, AK60v1.1, AK70, are AK80 the different CAN motors.
    	;Values 0(not used), AK60, AK60v1.1, AK70, AK80, MaxonMotor
	hip = AK60v1.1
	knee = 0
	ankle = AK80
	elbow = 0
    
    	;Joint gear ratio = velocity of driving member (motor)/velocity of the driven member (output shaft), assumes constant gearing ratio. If the motor spins 6 revolutions to 1 revolution of the output this value would be 6.
    	;This is for transmission gearing after the motor output shaft. If the Motor has a built in gearing that should be part of the motor class (see motor.h/.cpp)
    	;Values 1, 2, 3, 4.5
	hipGearRatio = 1
	kneeGearRatio = 1
	ankleGearRatio = 4.5
	elbowGearRatio = 4.5

	;Default controller for the joint
	;Hip Controllers: zeroTorque, franksCollinsHip, constantTorque, chirp, step, phmc
	;Knee Controllers: zeroTorque, constantTorque, chirp, step
	;Ankle Controllers: zeroTorque, PJMC, zhangCollins, constantTorque, TREC, calibrManager, chirp, step, SPV2 
	;Elbow Controllers: zeroTorque, elbowMinMax, calibrManager, chirp, step
	hipDefaultController = franksCollinsHip
	kneeDefaultController = 0
	ankleDefaultController = PJMC
	elbowDefaultController = 0
    
    	;Do you want to use a torque sensor for these joints, 0 = no, yes = yes
	hipUseTorqueSensor = 0
	kneeUseTorqueSensor = 0
	ankleUseTorqueSensor = 0
	elbowUseTorqueSensor = 0

	;Flip direction for the motor cmd, 0 neither, left, right, both
	hipFlipMotorDir = left
	kneeFlipMotorDir = 0
	ankleFlipMotorDir = left
	elbowFlipMotorDir = 0

	;Flip direction for the torque sensor readings, 0 neither, left, right, both
	hipFlipTorqueDir = right
	kneeFlipTorqueDir = 0
	ankleFlipTorqueDir = right
	elbowFlipTorqueDir = 0

	;Flip direction for the angle sensor readings, 0 neither, left, right, both
	hipFlipAngleDir = 0
	kneeFlipAngleDir = 0
	ankleFlipAngleDir = 0
	elbowFlipAngleDir = 0

	;Exoskeleton joint range of motion in degrees
	leftHipRoM = 0
	rightHipRoM = 0
	leftKneeRoM = 0
	rightKneeRoM = 0
	leftAnkleRoM = 0
	rightAnkleRoM = 0
	leftElbowRoM = 0
	rightElbowRoM = 0
	
	;Torque sensor calibration results, a value of "255" leads to the calibration value being utilizied
	leftHipTorqueOffset = 255
	rightHipTorqueOffset = 255
	leftKneeTorqueOffset = 255
	rightKneeTorqueOffset = 255
	leftAnkleTorqueOffset = 255
	rightAnkleTorqueOffset = 255
	leftElbowTorqueOffset = 255
	rightElbowTorqueOffset = 255
    
[bilateralHip]
	;Sides - left, right, bilateral	
	sides = bilateral

	;Joints used and their motor name, 0 = not useed, AK60, AK60v1.1, AK70, are AK80 the different CAN motors.
    	;Values 0(not used), AK60, AK60v1.1, AK70, AK80, MaxonMotor
	hip = AK60v1.1
	knee = 0
	ankle = 0
	elbow = 0
    
    	;Joint gear ratio = velocity of driving member (motor)/velocity of the driven member (output shaft), assumes constant gearing ratio. If the motor spins 6 revolutions to 1 revolution of the output this value would be 6.
    	;This is for transmission gearing after the motor output shaft. If the Motor has a built in gearing that should be part of the motor class (see motor.h/.cpp)
    	;Values 1, 2, 3, 4.5
	hipGearRatio = 1
	kneeGearRatio = 1
	ankleGearRatio = 4.5
	elbowGearRatio = 4.5

	;Default controller for the joint
	;Hip Controllers: zeroTorque, franksCollinsHip, constantTorque, chirp, step, phmc
	;Knee Controllers: zeroTorque, constantTorque, chirp, step
	;Ankle Controllers: zeroTorque, PJMC, zhangCollins, constantTorque, TREC, calibrManager, chirp, step, SPV2 
	;Elbow Controllers: zeroTorque, elbowMinMax, calibrManager, chirp, step
	hipDefaultController = franksCollinsHip
	kneeDefaultController = 0
	ankleDefaultController = 0
	elbowDefaultController = 0
    
    	;Do you want to use a torque sensor for these joints, 0 = no, yes = yes
	hipUseTorqueSensor = 0
	kneeUseTorqueSensor = 0
	ankleUseTorqueSensor = 0
	elbowUseTorqueSensor = 0

	;Flip direction for the motor cmd, 0 neither, left, right, both
	hipFlipMotorDir = left
	kneeFlipMotorDir = 0
	ankleFlipMotorDir = 0
	elbowFlipMotorDir = 0

	;Flip direction for the torque sensor readings, 0 neither, left, right, both
	hipFlipTorqueDir = right
	kneeFlipTorqueDir = 0
	ankleFlipTorqueDir = 0
	elbowFlipTorqueDir = 0

	;Flip direction for the angle sensor readings, 0 neither, left, right, both
	hipFlipAngleDir = 0
	kneeFlipAngleDir = 0
	ankleFlipAngleDir = 0
	elbowFlipAngleDir = 0
	
	;Exoskeleton joint range of motion in degrees
	leftHipRoM = 0
	rightHipRoM = 0
	leftKneeRoM = 0
	rightKneeRoM = 0
	leftAnkleRoM = 0
	rightAnkleRoM = 0
	leftElbowRoM = 0
	rightElbowRoM = 0
	
	;Torque sensor calibration results, a value of "255" leads to the calibration value being utilizied
	leftHipTorqueOffset = 255
	rightHipTorqueOffset = 255
	leftKneeTorqueOffset = 255
	rightKneeTorqueOffset = 255
	leftAnkleTorqueOffset = 255
	rightAnkleTorqueOffset = 255
	leftElbowTorqueOffset = 255
	rightElbowTorqueOffset = 255
    
[bilateralAnkle]
	;Sides - left, right, bilateral	
	sides = bilateral

	;Joints used and their motor name, 0 = not useed, AK60, AK60v1.1, AK70, are AK80 the different CAN motors.
    	;Values 0(not used), AK60, AK60v1.1, AK70, AK80, MaxonMotor, MaxonMotor
	hip = 0
	knee = 0
	ankle = AK80
	elbow = 0
    
    	;Joint gear ratio = velocity of driving member (motor)/velocity of the driven member (output shaft), assumes constant gearing ratio. If the motor spins 6 revolutions to 1 revolution of the output this value would be 6.
    	;This is for transmission gearing after the motor output shaft. If the Motor has a built in gearing that should be part of the motor class (see motor.h/.cpp)
    	;Values 1, 2, 3, 4.5
	hipGearRatio = 1
	kneeGearRatio = 1
	ankleGearRatio = 4.5
	elbowGearRatio = 4.5

	;Default controller for the joint
	;Hip Controllers: zeroTorque, franksCollinsHip, constantTorque, chirp, step, phmc
	;Knee Controllers: zeroTorque, constantTorque, chirp, step
	;Ankle Controllers: zeroTorque, PJMC, zhangCollins, constantTorque, TREC, calibrManager, chirp, step, SPV2 
	;Elbow Controllers: zeroTorque, elbowMinMax, calibrManager, chirp, step
	hipDefaultController = 0
	kneeDefaultController = 0
	ankleDefaultController = calibrManager
	elbowDefaultController = 0
    
    	;Do you want to use a torque sensor for these joints, 0 = no, yes = yes
	hipUseTorqueSensor = 0
	kneeUseTorqueSensor = 0
	ankleUseTorqueSensor = yes
	elbowUseTorqueSensor = 0

	;Flip direction for the motor cmd, 0 neither, left, right, both
	hipFlipMotorDir = 0
	kneeFlipMotorDir = 0
	ankleFlipMotorDir = left
	elbowFlipMotorDir = 0

	;Flip direction for the torque sensor readings, 0 neither, left, right, both
	hipFlipTorqueDir = 0
	kneeFlipTorqueDir = 0
	ankleFlipTorqueDir = right
	elbowFlipTorqueDir = 0

	;Flip direction for the angle sensor readings, 0 neither, left, right, both
	hipFlipAngleDir = 0
	kneeFlipAngleDir = 0
	ankleFlipAngleDir = 0
	elbowFlipAngleDir = 0
	
	;Exoskeleton joint range of motion in degrees
	leftHipRoM = 0
	rightHipRoM = 0
	leftKneeRoM = 0
	rightKneeRoM = 0
	leftAnkleRoM = 0
	rightAnkleRoM = 0
	leftElbowRoM = 0
	rightElbowRoM = 0
	
	;Torque sensor calibration results, a value of "255" leads to the calibration value being utilizied
	leftHipTorqueOffset = 255
	rightHipTorqueOffset = 255
	leftKneeTorqueOffset = 255
	rightKneeTorqueOffset = 255
	leftAnkleTorqueOffset = 255
	rightAnkleTorqueOffset = 255
	leftElbowTorqueOffset = 255
	rightElbowTorqueOffset = 255
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

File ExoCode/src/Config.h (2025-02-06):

/**
 * @file Config.h
 * @author Chancelor Cuddeback
 * @brief Configuration variables for the codebase.
 * @date 2023-07-18
 * 
 */

#ifndef Config_h
#define Config_h 

#include "Arduino.h"
#include "LogLevels.h"
    #define FIRMWARE_VERSION 0_1_0

    #define AK_Board_V0_1 1
    #define AK_Board_V0_3 2
    #define AK_Board_V0_4 3
    #define AK_Board_V0_5_1 4
	#define AK_Board_V0_6_Maxon 5

    #define BOARD_VERSION AK_Board_V0_5_1             
    #define REAL_TIME_I2C 1
    #define LOOP_FREQ_HZ 500
    #define LOOP_TIME_TOLERANCE 0.1 
    
    #define USE_SPEED_CHECK 0
	#define USE_ANGLE_SENSORS 1

    //MACRO magic to convert a define to a string
    #define VAL(str) #str
    #define TOSTRING(str) VAL(str)

    namespace logging
    {
        const LogLevel level = LogLevel::Release; //Release or Debug (Note: Enter Debug to have Logger print to serial monitor)
        const int baud_rate = 115200;
    }
    
    namespace sync_time
    {
        const unsigned int NUM_START_STOP_BLINKS = 1;                                   //The number of times to have the LED on during the start stop sequence
        const unsigned int SYNC_HALF_PERIOD_US = 125000;                                //Half blink period in micro seconds
        const unsigned int SYNC_START_STOP_HALF_PERIOD_US = 4 * SYNC_HALF_PERIOD_US;    //Half blink period for the begining and end of the sequence. This is usually longer so it is easy to identify.
    }

    namespace fsr_config
    {
        const float FSR_UPPER_THRESHOLD = 0.25;
        const float FSR_LOWER_THRESHOLD = 0.15;
        const float SCHMITT_DELTA = (FSR_UPPER_THRESHOLD - FSR_LOWER_THRESHOLD)/2;
    }
	
	namespace angle_sensor
	{
		const float ANGLE_UPPER_THRESHOLD = 0.9;
		const float ANGLE_LOWER_THRESHOLD = 0.1;
		const float ROM_LEFT = 103.2f;
		const float ROM_RIGHT = 91.4f; //In degrees
	}

    namespace analog
    {
        const float RESOLUTION = 12;    //The resolution of the analog to digital converter
        const float COUNTS = 4096;      //The number of counts the ADC can have
    }
    
    namespace torque_calibration
    {
        const float AI_CNT_TO_V = 3.3 / 4096;   //Conversion from count to voltage
        const float TRQ_V_TO_NM = 53.70;        //Conversion from voltage to Nm (Negative do to mismatch in torque sensor and motor torque directions) S12:(Left) = 39.8, S05 (Right) = 44.6; (These will be sensor specific).
    }

    namespace BLE_times
    {
        const float _status_msg_delay = 2000000;    //Microseconds
        const float _real_time_msg_delay = 20000;   //Microseconds
        const float _update_delay = 1000;           //Microseconds
        const float _poll_timeout = 4;              //Milliseconds
    }
    
    //Update this namespace for future exo updates to display correct information on app
    namespace exo_info
    {
        const String FirmwareVersion = String(TOSTRING(FIRMWARE_VERSION));  //String to add to firmware char
        const String PCBVersion = String(TOSTRING(BOARD_VERSION));          //String to add to pcb char
        const String DeviceName = String("Exo");                            //String to add to device char, if you would like the system to set it use "NULL"
    }

    namespace UART_times
    {
        const float UPDATE_PERIOD = 1000;       //Microseconds, time between updating data over uart
        const float COMS_MCU_TIMEOUT = 5000;    //Microseconds
        const float CONT_MCU_TIMEOUT = 1000;    //Microseconds
        const float CONFIG_TIMEOUT = 8000;      //Milliseconds
    }

#endif

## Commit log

2023-04-13 Babys first commit
    [PJMC.csv, bangBang.csv, constantTorque.csv, elbowMinMax.csv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]
2023-04-24 Updated to reflect the most recent changes in the old repo
    [elbowMinMax.csv, ptbGeneral.csv]
2023-04-26 Create Direction Calibration.md
2023-04-27 Changed supportive term to include level calibration
2023-05-18 Restore timeout value and disable debug prints
2023-06-09 Implemented Joint.cpp changes for ErrorManager. Also added the error reporter. Not runtime tested.
2023-06-26 Tested for runtiime and implmented a couple of cases. Torque errors were triggering before the calibration, but now the error manager only runs when the status is correct.
2023-06-28 Fix error reporting type for motor timeouts
2023-07-17 Errors now disable motors
2023-09-08 Added smoothing to the torque error. Spikes in the current reading were causing the torque error to spike, this should limit that and we will be able to set more realistic error bounds.
2023-09-12 Jack's updated code - removes controllers that are not used and adds in Hip Resistance, Chirp, and Step Controllers
    [bangBang.csv, chirp.csv, extensionAngle.csv, gaitPhase.csv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]
2023-09-14 Added TREC (GAsP) .csv; Fixes bugs related to (1) plotting and (2) updating advanced parameters in a muli-joint condition (e.g., updating ankle parameters set hip to defualt too)
    [GAsP.csv]
2023-09-14 Fixed serial prints used for troubleshooting
2024-03-18 Maxon motor spinning
2024-05-28 Updated Readme with current known issues. Added I gain to PID, corrected issues in PJMC controller, added torque sensor capabilities to Hip franksCollins Controller. Added in regression equation capa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
2024-05-29 Added in up to date Elbow Control
    [elbowMinMax.csv]
2024-06-28 Updated Guide, Style, and Formatting of Some Sections, Removed De-enable of motors when Error thrown (for troubleshooting purposes).
2024-08-19 Removed unused controllers, removed unused motor type, standardized naming convention of TREC, cleaned up and commented controller code section.
    [heelToe.csv, hipResist.csv, ptbGeneral.csv, stasis.csv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]
2024-08-20 Added Elbow Joint
2024-08-21 Fixed config formatting, removed unused config piece, added new config component to include torque sensor usage flag and updated code to properly utilize
    [PJMC.csv, chirp.csv, constantTorque.csv, elbowMinMax.csv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]
2024-08-26 Changed "Leg" terminology to "Side" to reflect multi-limb and upper- and lower-extremity nature fo the device
2024-08-26 Fixed Elbow Controller Parameter Definintions to Match Other Joints.
2024-09-04 SPVS Battery Test
2024-09-12 Added Hardware to Codebase
    [7804K143_Stainless Steel Ball Bearing.SLDPRT, 90236A127_M3x35_1Zinc-Plated Alloy Steel Torx Flat Head Screws.SLDPRT, 91290A117_M3x12_6Alloy Steel Socket Head S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]
2024-09-13 Updated Hardware section to include Large Cable Transmission System, Added in Publication Experimental Data
    [Back_Cover_AK60V1_1(1).SLDPRT, Bill_of_Materials_AK60V1_1.xlsx, Bill_of_Materials_AK70.xlsx, Bill_of_Materials_AK80.xlsx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]
2024-10-02 Servo now works
2024-10-03 30-degree servo sweep
2024-10-08 Test version 1
    Motor works, servo not responding
2024-10-08 Servo works, motor works
    Servo would stop responding after some time
2024-10-09 ver 0.7
    SD parameters work, servo works, motor works
2024-10-10 v0.8
    Servo stays standby while plantarflexion assist from the leaf spring is sufficient
2024-10-11 Untested version
    Motor and servo most likely won't work. This version is to test the Maxon motor standby function.
2024-10-11 Untested version 2
    All plots will be multiplied by -1 when the Maxon motors has just been reset. Little bugs might exist.
2024-10-11 Untested version 3
    On top of Untested version 2, now the servo should automatically return to the home position when switched off manually.
2024-10-17 New Hope
    Motor reset seems to be working?
2024-10-17 New Hope II
    This version enables the motor right away
2024-10-18 Force calibrate heel FSR with toe FSR
2024-11-07 SPV2 With Standardized Maxon Motor Implementation
    PID needs some tuning
2024-11-13 PWM new boundaries & FSR-based motor standby
2024-11-15 Servo comes home after 200 ms
2024-11-19 Servo control with map() and constrain()
2024-11-21 Fixed the Nano 33 BLE compiling issue
    Servo control code has been reverted
2024-11-21 Added Proportional Hip Moment Controller (PHMC), works but needs to be ironed out a bit more for reliability. Also fixed bug realted to calculation of moving average in Side.cpp, all in realtion to e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
    [PHMC.csv]
2024-11-26 Motor cmd during zero-torque and swing limited
    Limited to ±300
2024-11-26 Servo control updated
2024-12-02 Frog Leap: 2nd Jump
    Generic PJMC function implemented. Torque sensor offset now can be pulled from the SD Card. SPV2 (controller ID: 11) controller has been created.
2024-12-03 Simplified servo control
    SPV2 servo behavior is a mess when not walking
2025-01-06 Updated GUI, Added Documentation Regarding Sensors, Added Heat Shields
    [ak60v1_1HeatShield.SLDPRT, ak80HeatShield.SLDPRT, hipHeatShield.SLDPRT]
2025-01-06 Activate the servo only when the SD card parameters are imported
2025-01-09 Added Saftey Overview Document and Updated Publication Data Section with new data
    [Duration_Test_Results.xlsx]
2025-01-15 Updated SD Card files
    [spv2.csv]
2025-02-06 Reviewed recent changes to code and updated comments to reflect current state
    [elbowMinMax.csv]
